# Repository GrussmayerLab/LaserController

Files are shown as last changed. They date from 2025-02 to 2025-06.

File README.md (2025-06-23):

# Laser Controller Project

## TL;DR (Quick Setup)

1. **Assemble the PCB**: 
   - Order the PCB from [JLCPCB](https://cart.jlcpcb.com) for ~$100 using the `gerber.zip`, `bom.csv`, and `laser_controller-top-pos.csv` files.
   - Use compatible [JST cables](https://www.amazon.nl/-/en/Mini-Micro-150mm-Cable-Female/dp/B01DU9OY40).

2. **Install MicroManager 2.0**:
   - Download and install [MicroManager 2.0](https://download.micro-manager.org/nightly/2.0/Windows/).

3. **Copy Files**:
   - Copy the precompiled `EMU` folder and `mmgr_dal_GrussmayerLab-LaserController.dll` into the root directory of MicroManager.

4. **Use the LaserControlGUI Plugin**:
   - Run MicroManager, open the **LaserControlGUI** plugin from **EMU**, and start controlling the laser!

---

This repository consists of the hardware, firmware, and software design for the Laser Controller system. It is divided into four main sections:

- **Electronics**: Schematic and PCB design files for the laser controller.
- **LaserControlFirmware**: C/C++ firmware for the Raspberry Pi Pico.
- **GrussmayerLab-LaserController**: C++ Micromanager Device Adapter to drive the laser controller.
- **LaserControlGUI**: Java-based plugin for Micromanager, built upon the EMU plugin.

## Table of Contents

- [Overview](#overview)
- [Folders](#folders)
  - [Electronics](#electronics)
  - [LaserControlFirmware](#lasercontrolfirmware)
  - [LaserControllerUI](#lasercontrollerui)
- [Getting Started](#getting-started)
  - [Hardware Setup](#hardware-setup)
  - [Firmware Setup](#firmware-setup)
  - [Software Setup](#software-setup)
- [Usage](#usage)
- [Contributing](#contributing)
- [License](#license)

## Overview

The Laser Controller project integrates hardware and software components to control a laser system. It consists of:

1. **Hardware**: Electronics, including a schematic and PCB design, for laser control.
2. **Firmware**: Raspberry Pi Pico firmware (C/C++) managing communication with the hardware.
3. **Software**: A Java plugin for MicroManager, based on the EMU plugin framework, along with a C++ Device Adapter for MicroManager.

## Folders

### Electronics

This folder contains the hardware designs for the laser controller:

- **Schematic**: Electrical design for the laser control system.
- **PCB Design**: Printed circuit board design files created using KiCAD.

Files in this folder:
- `schematic.kicad_sch`: Schematic file.
- `pcb.kicad_pcb`: PCB design file.

For more details, refer to the [KiCAD Documentation](https://kicad.org/documentation/).

### LaserControlFirmware

Firmware for the Raspberry Pi Pico, written in C/C++, responsible for controlling the laser system.

Files in this folder:
- `main.cpp`: Main program code.
- `CMakeLists.txt`: CMake configuration.
- `README.md`: Firmware setup instructions.

### LaserControlGUI

Java-based plugin for Micromanager, allowing control of the laser system.

Files in this folder:
- `LaserPanel.java`: Laser slide panel code.
- `MyFrame.java`: Main plugin UI containing multiple LaserPanel instances.
- `MyPlugin.java`: Main plugin class implementing the UIPlugin interface.

## Getting Started

### Hardware Setup

1. **Review Hardware Files**: Use KiCAD to view schematic and PCB design files in the `Electronics` folder.
2. **Assemble the PCB**: Using `gerber.zip`, `bom.csv`, and `laser_controller-top-pos.csv`, you can assemble your PCB at [JLCPCB](https://cart.jlcpcb.com) for approximately $100.
3. **Connect Components**: The board has **JST S3B-PH-K-S (LF)(SN)** connectors. Buy [compatible cables](https://www.amazon.nl/-/en/Mini-Micro-150mm-Cable-Female/dp/B01DU9OY40) and modify them as needed.

### Firmware Setup

1. **Flashing Precompiled Firmware**:
   - The compiled UF2 firmware is already included in the repository.
   - Hold the **BOOTSEL** button on the Raspberry Pi Pico, connect it to a PC via USB, and it will appear as a **USB drive**.
   - Copy the UF2 file to the drive, and the Pico is programmed.

2. **Optional: Building from Source**:
   If you wish to modify the firmware, install the following tools:
   - [Raspberry Pi Pico SDK](https://github.com/raspberrypi/pico-sdk)
   - [CMake](https://cmake.org/)
   - [ARM GCC Toolchain](https://developer.arm.com/tools-and-software/openSourceTools/gnu-toolchain/gnu-toolchain-r)

   Clone the repository and build:
   ```bash
   git clone https://github.com/GrussmayerLab/LaserController.git
   cd LaserControlFirmware
   mkdir build
   cd build
   cmake ..
   make
   ```

### Software Setup

1. **Install MicroManager 2.0**:
   - Download and install the latest version of [MicroManager 2.0](https://download.micro-manager.org/nightly/2.0/Windows/). Copy the precompiled `EMU` folder (provided) into the root directory of MicroManager.

2. **Install the EMU Plugin** (for source code editing):
   - If you wish to modify or extend the plugin, follow the instructions on how to install [EMU](https://jdeschamps.github.io/EMU-guide/):

3. **Install LaserControlGUI Plugin**:
   - To enable the LaserControlUI plugin, export the Java project from Eclipse into the EMU folder in MicroManager.

4. **Install the Device Adapter**:
   - Copy the `mmgr_dal_GrussmayerLab-LaserController.dll` file in the root directory of MicroManager.
   - If you need to configure or extend the device adapter, follow the [MicroManager Visual Studio setup guide](https://micro-manager.org/Visual_Studio_project_settings_for_device_adapters). After setting up your project, place `.h` files in the header folder and `.cpp` files in the source folder. Compile the project, and place the resulting `.dll` file in the root directory of MicroManager.

## Usage

1. Start MicroManager.
2. Open the **LaserControlGUI** plugin.
3. The plugin will interface with the Raspberry Pi Pico, allowing laser control via MicroManager.

## License

This project is licensed under the MIT License - see the LICENSE file for details.

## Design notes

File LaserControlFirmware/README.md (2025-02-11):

# Laser Controller Software

## Overview

Laser controller which can be controlled over serial USB via uManager custom EMU plugin.

## Installation
1. Clone the repository: `https://github.com/GrussmayerLab/LaserController.git`

2. Set up the Pico SDK:
   - Download and extract the Pico SDK from [https://github.com/raspberrypi/pico-sdk](https://github.com/raspberrypi/pico-sdk).
   - Configure the CMakeLists.txt file according to your project's requirements.
   - Install Visual Studio Code and the necessary extensions (C/C++ and CMake Tools).
   - Open the Pico SDK folder in Visual Studio Code.
   - Build the project using the provided build tasks.

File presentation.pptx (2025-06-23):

## Laser Controller

## Current Solution

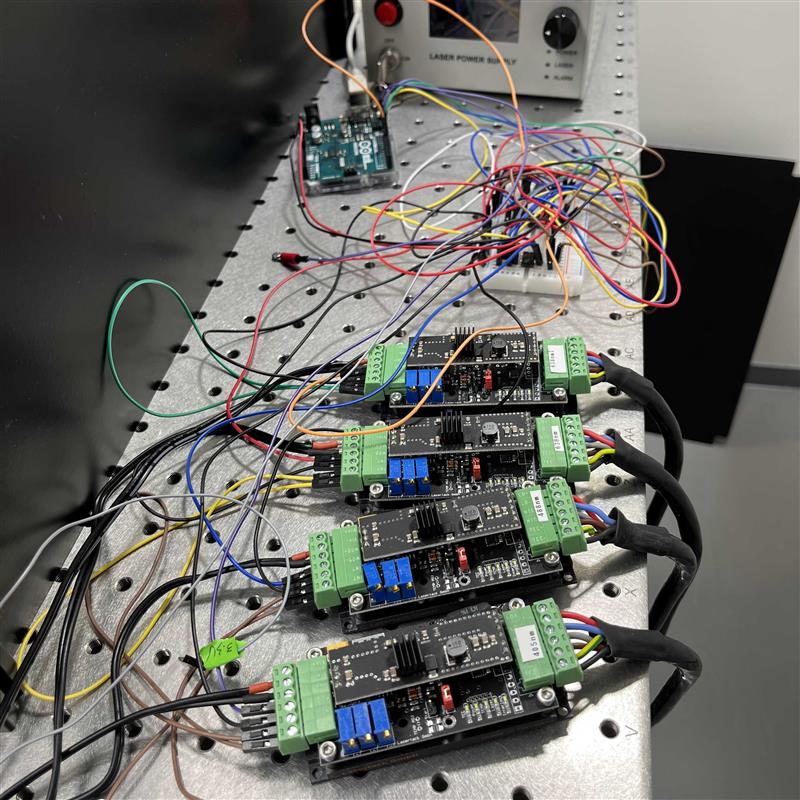
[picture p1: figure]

## Requirements

- Should be controllable in Micro-Manager
- Should be easy to install (software)
- Should be easy to build (hardware)
- Should be inexpensive (under $100)

## Hardware Design

Raspberry Pi Pico: firmware can easily be installed without requiring special tools.
The Board can be ordered at JLC PCB at a cost of ~$35 per board.

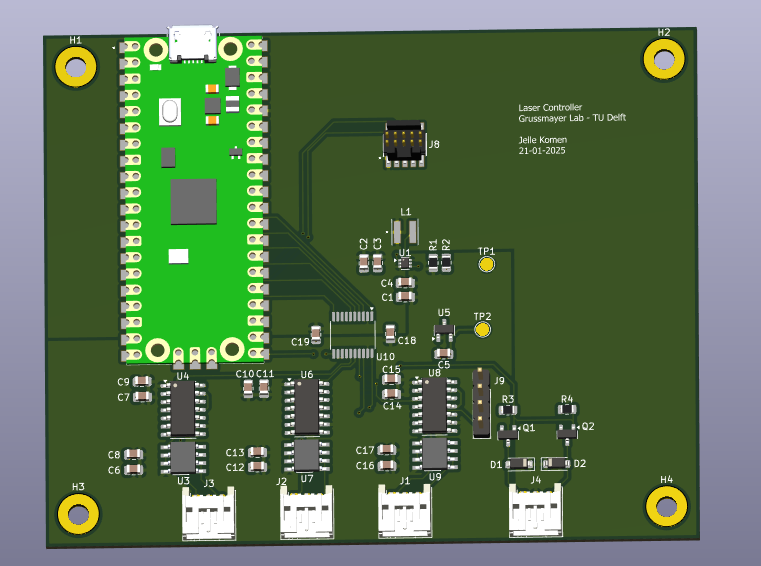
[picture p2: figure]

## Software Design

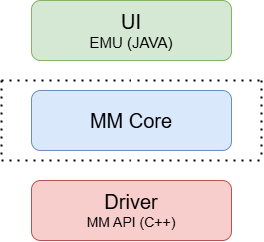
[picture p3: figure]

## Driver Installation

- Open Device Manager

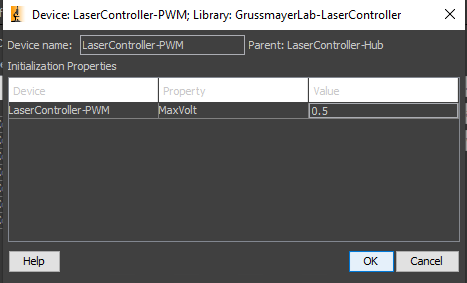
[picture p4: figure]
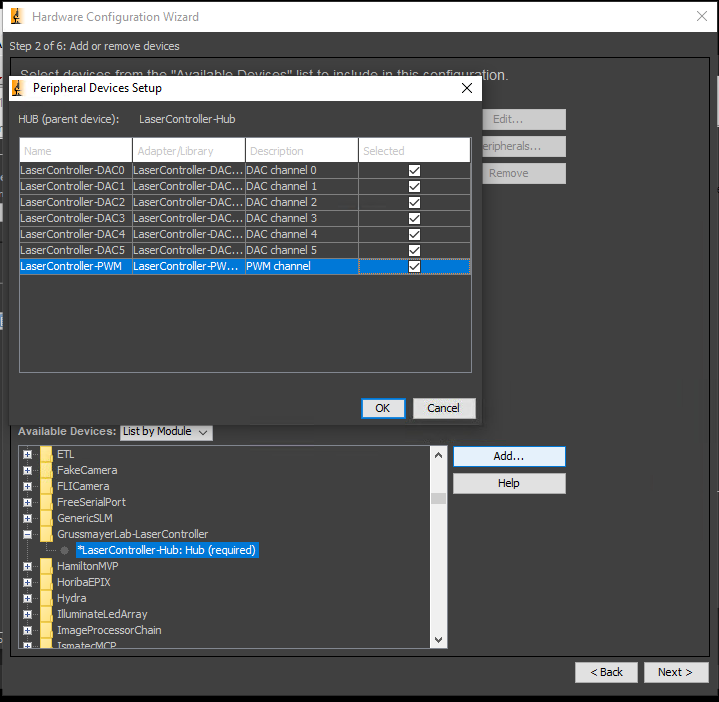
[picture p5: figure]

## User Interface

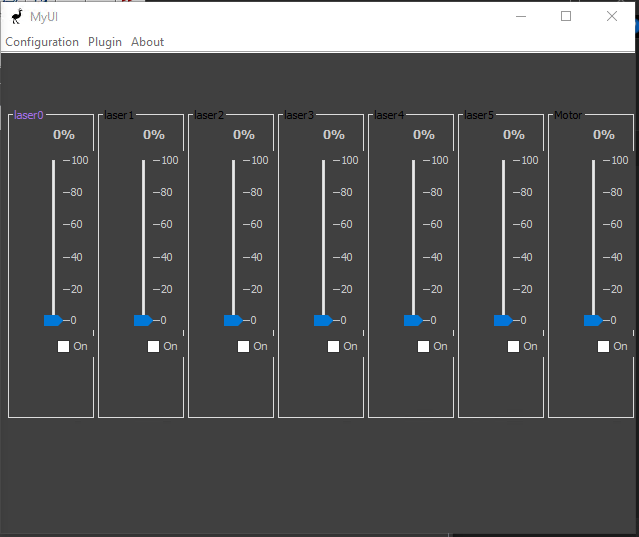
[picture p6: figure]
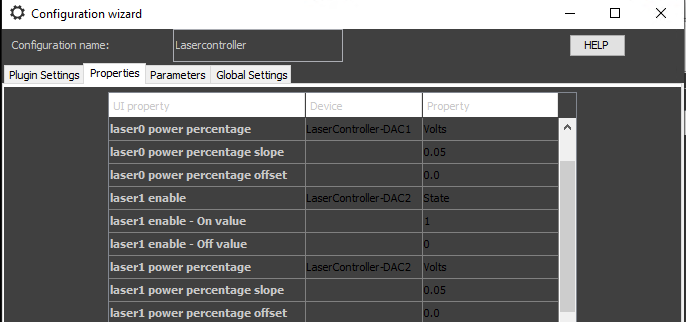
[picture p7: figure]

## Questions?

https://github.com/GrussmayerLab/LaserController

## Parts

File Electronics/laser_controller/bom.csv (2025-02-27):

Comment | Designator | Footprint | LCSC
TXS0108EPW | "U10" | "Package_SO:Texas_PW0020A_TSSOP-20_4.4x6.5mm_P0.65mm" | "C17206"
REF3025-AIDBZR | U5 | Package_TO_SOT_SMD:SOT-23-3 | C11334
MCP4922-ESL | U4,U6,U8 | Package_SO:SOIC-14_3.9x8.7mm_P1.27mm | C39851
MCP6022 | U3,U7,U9 | Package_SO:SOIC-8_5.275x5.275mm_P1.27mm | C57639
TPS61023 | U1 | Package_TO_SOT_SMD:SOT-563 | C919459
10k | R3,R4 | Resistor_SMD:R_0805_2012Metric | C149504
100k | R2 | Resistor_SMD:R_0805_2012Metric | C441992
820k | R1 | Resistor_SMD:R_0805_2012Metric | C413229
AO3400A | Q1,Q2 | Package_TO_SOT_SMD:SOT-23 | C20917
XEL4030-102MEC | L1 | parts:IND_XEL4030-102MEC | C5441341
FTSH-105-01-F-DV-P-TR | J8 | parts:SAMTEC_FTSH-105-01-F-DV-P-TR | C5136979
SM4007PL | D1,D2 | Diode_SMD:D_SOD-123 | C64898
100n | C2,C6,C7,C11,C13,C15,C17,C18,C19 | Capacitor_SMD:C_0805_2012Metric | C1711
10u | C1,C3,C4,C5,C8,C9,C10,C12,C14,C16 | Capacitor_SMD:C_0805_2012Metric | C1713
S3B-PH-K-S_LF__SN_ | "J1 | J2 | J3 | J4" | Connector_JST:JST_PH_S3B-PH-K_1x03_P2.00mm_Horizontal | C157929

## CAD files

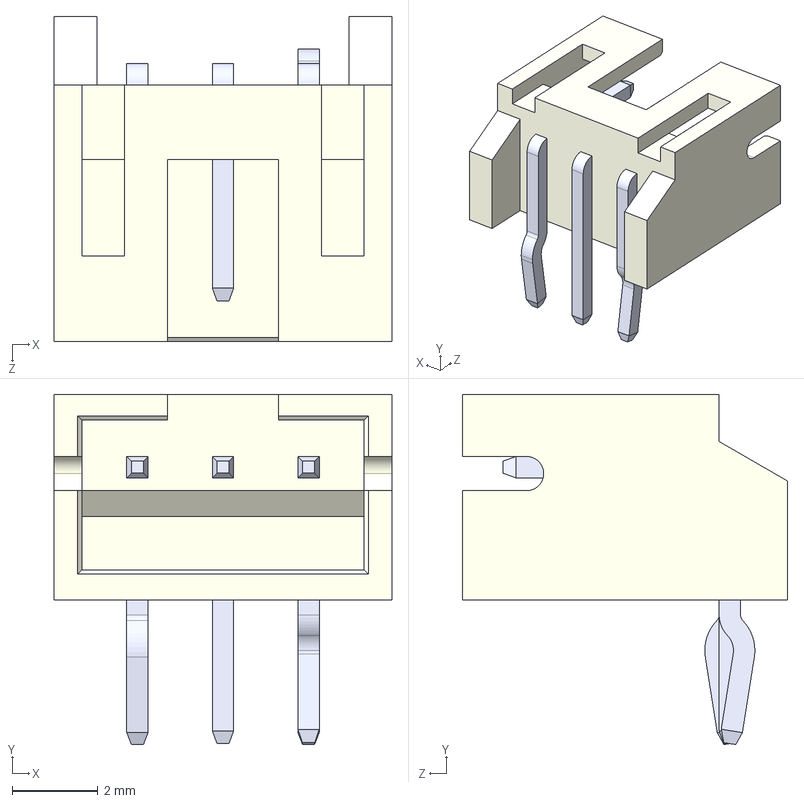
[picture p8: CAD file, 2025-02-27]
Electronics/laser_controller/parts/S3B-PH-K-S_LF__SN_.step
7.90 x 8.18 x 7.60 mm

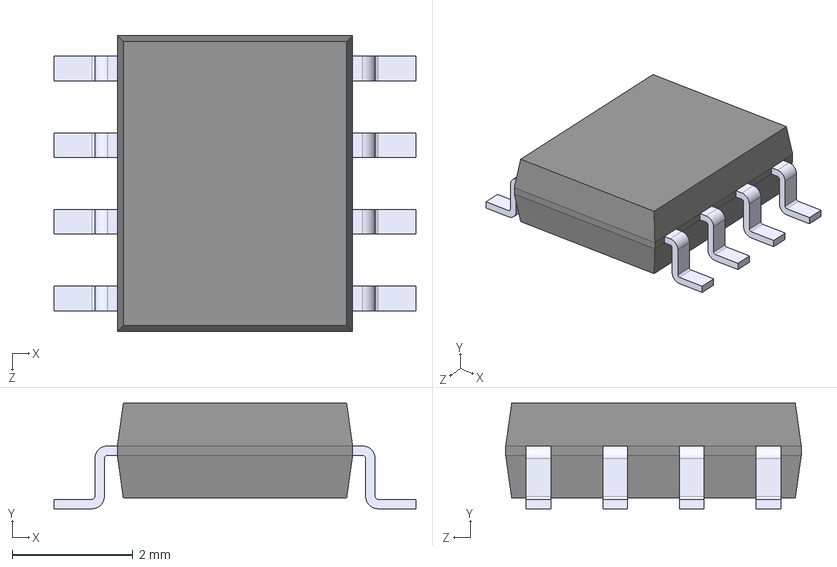
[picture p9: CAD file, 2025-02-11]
Electronics/laser_controller/parts/MCP6022T-I_SN.step
6.00 x 1.75 x 4.90 mm

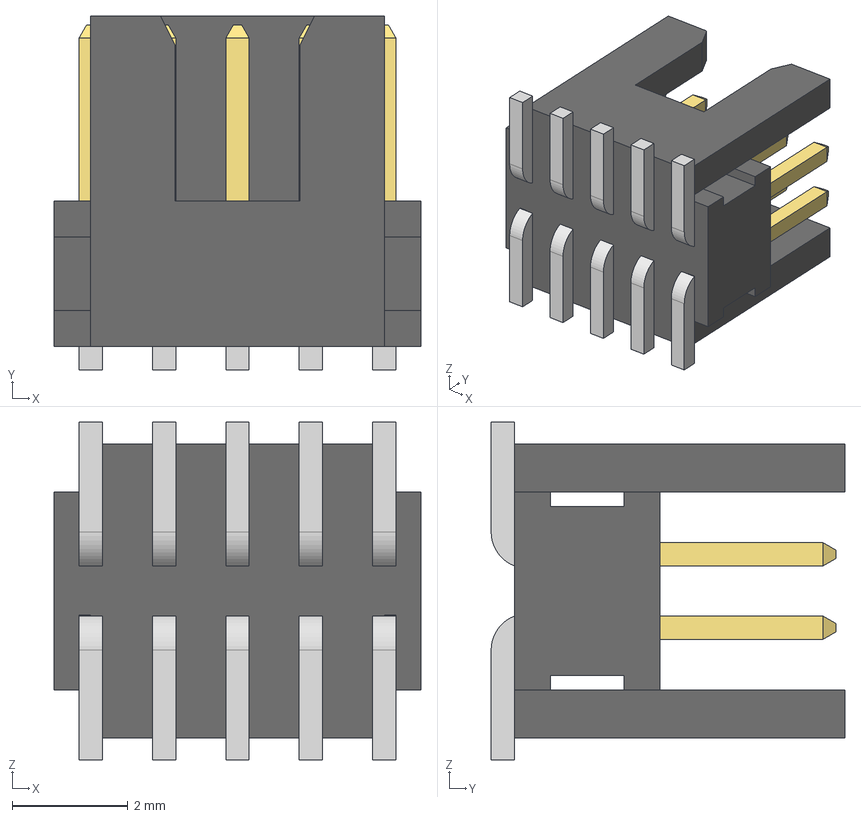
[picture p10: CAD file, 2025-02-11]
Electronics/laser_controller/parts/FTSH-105-01-F-DV-P-TR.step
6.35 x 6.12 x 5.84 mm
FTSH-105-01-F-DV-K_body
FTSH-105-01-F-DV-K_pins1
FTSH-105-01-F-DV-K_pins2

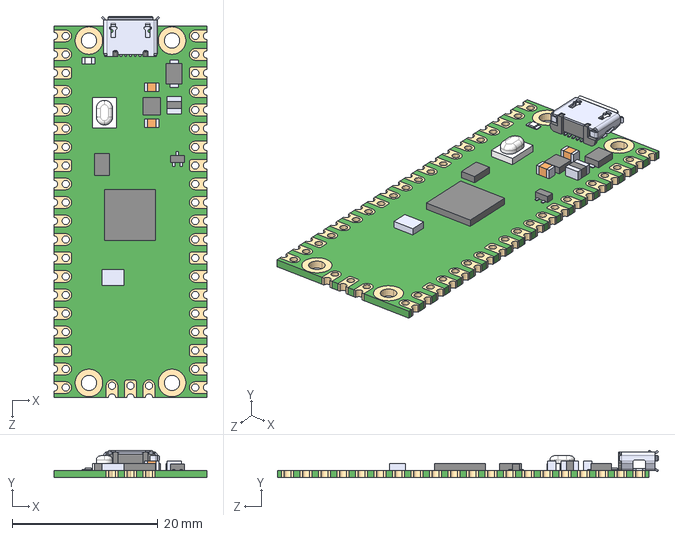
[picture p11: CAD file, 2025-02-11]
Electronics/laser_controller/parts/SC0915.step
21.0 x 3.73 x 52.3 mm

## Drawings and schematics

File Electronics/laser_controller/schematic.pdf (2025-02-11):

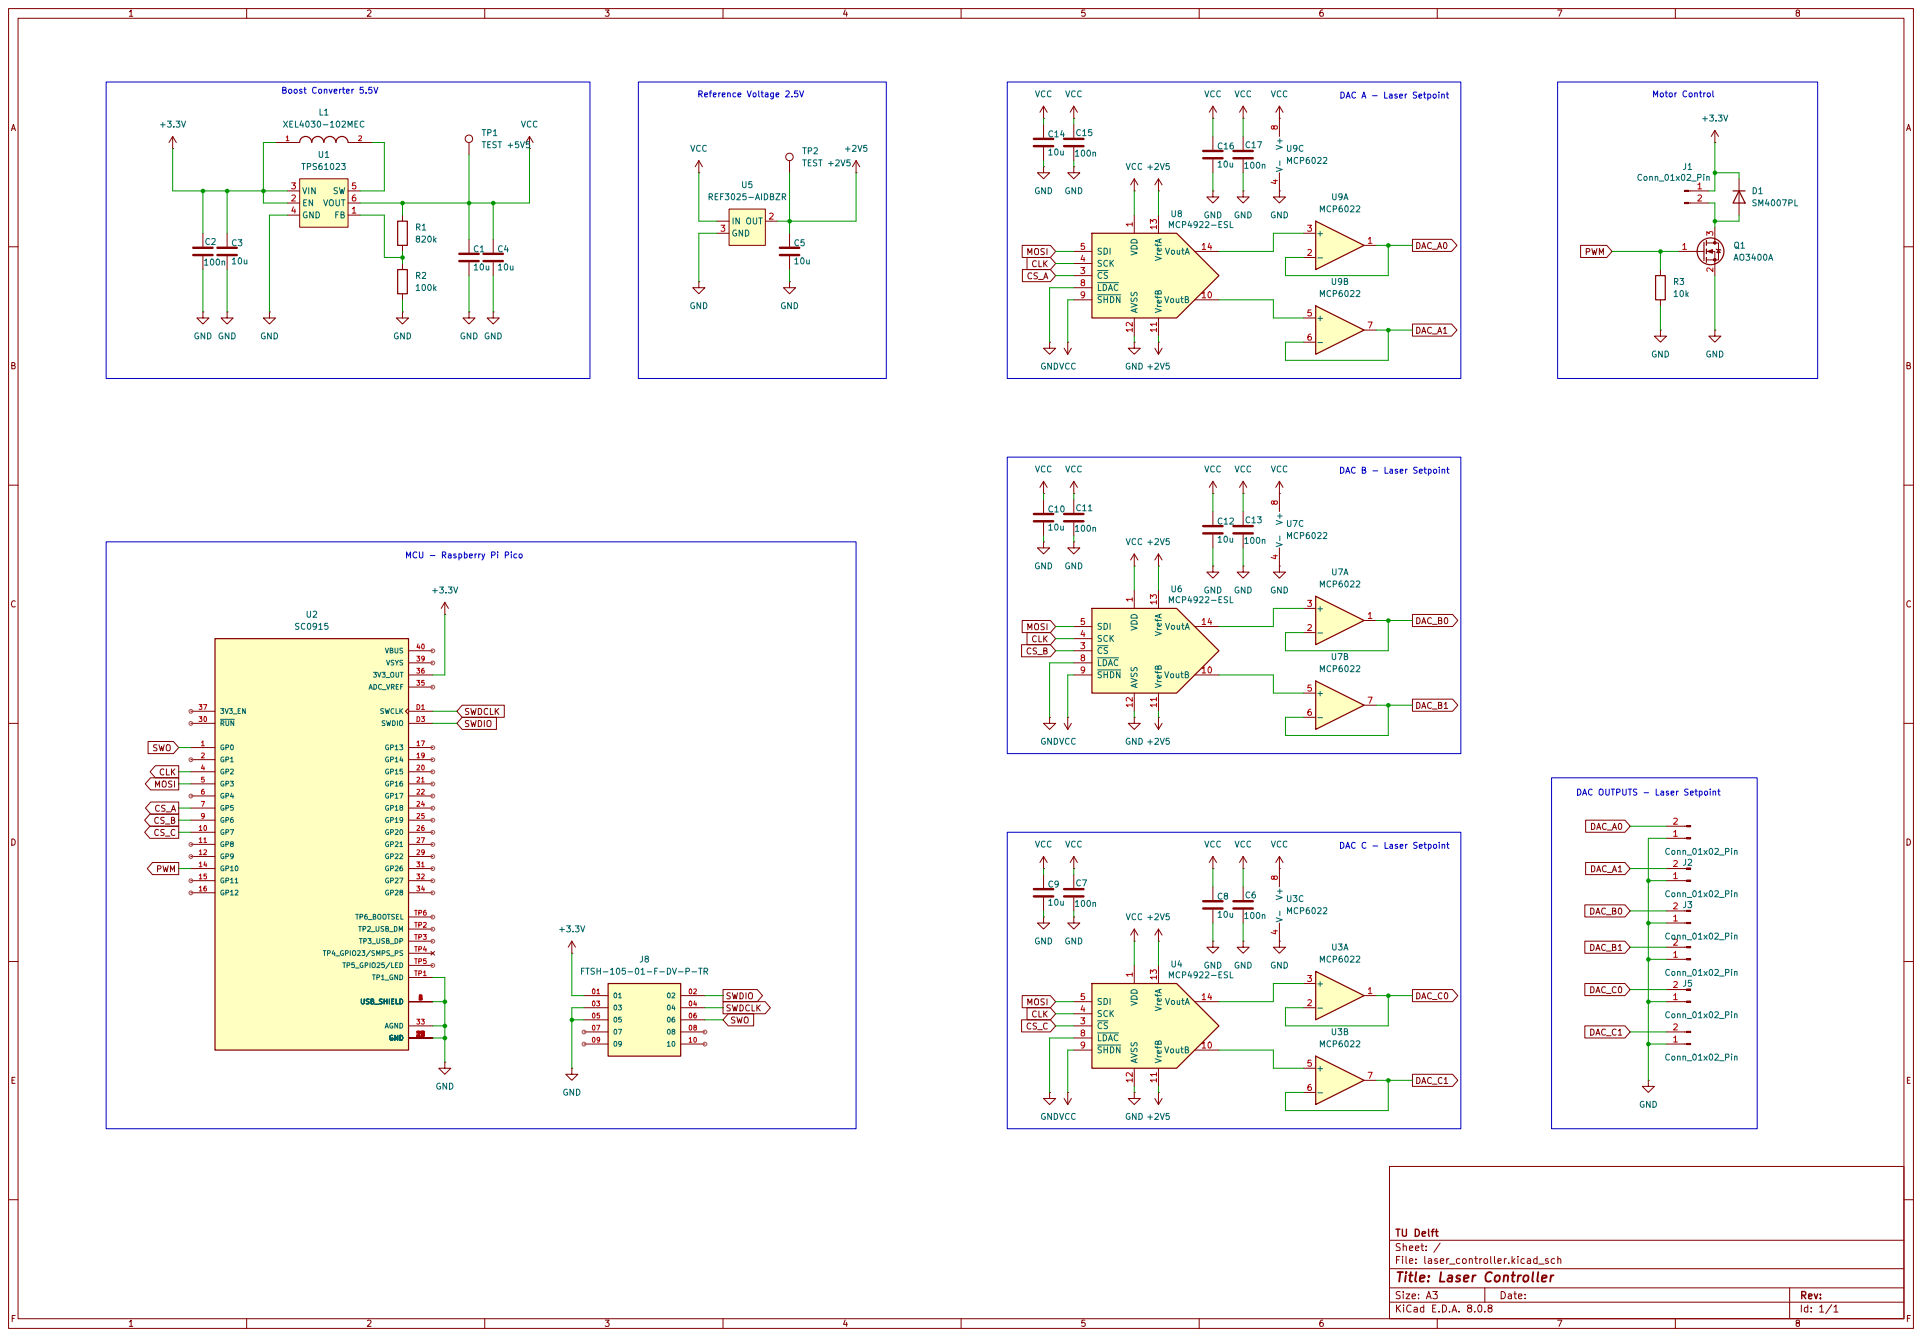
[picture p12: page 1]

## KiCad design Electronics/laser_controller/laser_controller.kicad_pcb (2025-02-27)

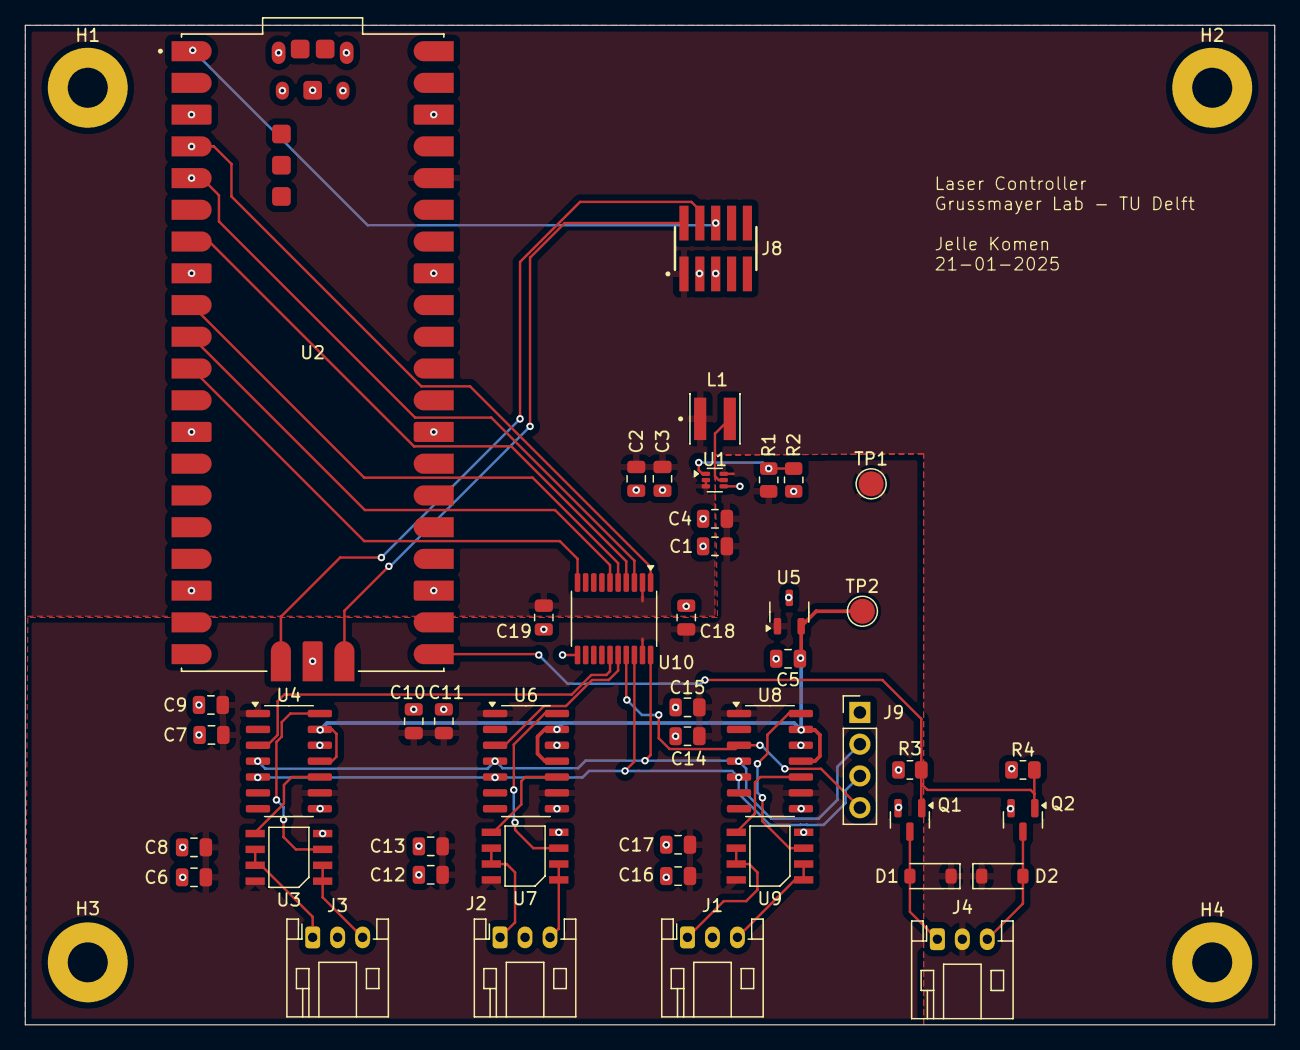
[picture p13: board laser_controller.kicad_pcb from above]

Board: 2 copper layers, 100.0 x 80.0 mm, 50 parts (0 on the bottom side), 35 nets.

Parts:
C1, C3, C4, C5, C8, C9, C10, C12, C14, C16: 10u; C_0805_2012Metric
C2, C6, C7, C11, C13, C15, C17, C18, C19: 100n; C_0805_2012Metric
D1, D2: SM4007PL; D_SOD-123
H1, H2, H3, H4: MountingHole_Pad; MountingHole_3.2mm_M3_Pad
J1, J2, J3, J4: S3B-PH-K-S_LF__SN_; JST_PH_S3B-PH-K_1x03_P2.00mm_Horizontal
J8: FTSH-105-01-F-DV-P-TR; SAMTEC_FTSH-105-01-F-DV-P-TR
J9: Conn_01x04_Pin; PinHeader_1x04_P2.54mm_Vertical
L1: XEL4030-102MEC; IND_XEL4030-102MEC
Q1, Q2: AO3400A; SOT-23
R1: 820k; R_0805_2012Metric
R2: 100k; R_0805_2012Metric
R3, R4: 10k; R_0805_2012Metric
TP1: TEST +5V5; TestPoint_Pad_D2.0mm
TP2: TEST +2V5; TestPoint_Pad_D2.0mm
U1: TPS61023; SOT-563
U2: SC0915; MODULE_SC0915
U3, U7, U9: MCP6022; SOIC-8-SN
U4, U6, U8: MCP4922-ESL; SOIC-14_3.9x8.7mm_P1.27mm
U5: REF3025-AIDBZR; SOT-23-3
U10: TXS0108EPW; Texas_PW0020A_TSSOP-20_4.4x6.5mm_P0.65mm

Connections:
+2V5: C5.1, TP2.1, U4.11 (VrefB), U4.13 (VrefA), U5.2 (OUT), U6.11 (VrefB), U6.13 (VrefA), U8.11 (VrefB), U8.13 (VrefA)
+3.3V: C2.1, C3.1, C19.1, D1.1 (K), D2.1 (K), J4.2, J8.01, L1.1, U1.2 (EN), U1.3 (VIN), U2.36 (3V3_OUT), U10.2 (VCCA)
CLK: U2.4 (GP2), U10.1 (A1)
CLK_B: J9.2, U4.4 (SCK), U6.4 (SCK), U8.4 (SCK), U10.20 (B1)
CS_A: U2.7 (GP5), U10.4 (A3)
CS_A_B: J9.4, U8.3 (~CS), U10.17 (B3)
CS_B: U2.9 (GP6), U10.5 (A4)
CS_B_B: U6.3 (~CS), U10.16 (B4)
CS_C: U2.10 (GP7), U10.6 (A5)
CS_C_B: U4.3 (~CS), U10.15 (B5)
DAC_A0: J1.3, U9.1, U9.2 (-)
DAC_A1: J1.1, U9.6 (-), U9.7
DAC_B0: J2.3, U7.1, U7.2 (-)
DAC_B1: J2.1, U7.6 (-), U7.7
DAC_C0: J3.3, U3.1, U3.2 (-)
DAC_C1: J3.1, U3.6 (-), U3.7
GND: C1.2, C2.2, C3.2, C4.2, C5.2, C6.2, C7.2, C8.2, C9.2, C10.2, C11.2, C12.2, C13.2, C14.2, C15.2, C16.2, C17.2, C18.2, C19.2, H1.1, H2.1, H3.1, H4.1, J1.2, J2.2, J3.2, J8.03, J8.05, J9.1, Q1.2 (S), Q2.2 (S), R2.2, R3.2, R4.2, U1.4 (GND), U2.3 (GND), U2.8 (GND), U2.13 (GND), U2.18 (GND), U2.23 (GND), U2.28 (GND), U2.33 (AGND), U2.38 (GND), U2.A (USB_SHIELD), U2.B (USB_SHIELD), U2.C (USB_SHIELD), U2.D (USB_SHIELD), U2.D2 (GND), U2.TP1 (TP1_GND), U3.4 (V-), U4.8 (~LDAC), U4.12 (AVSS), U5.3 (GND), U6.8 (~LDAC), U6.12 (AVSS), U7.4 (V-), U8.8 (~LDAC), U8.12 (AVSS), U9.4 (V-), U10.11 (GND)
MOSI: U2.5 (GP3), U10.3 (A2)
MOSI_B: J9.3, U4.5 (SDI), U6.5 (SDI), U8.5 (SDI), U10.18 (B2)
Motor- A: D1.2 (A), J4.1, Q1.3 (D)
Motor- B: D2.2 (A), J4.3, Q2.3 (D)
unnamed: R1.2, R2.1, U1.1 (FB)
unnamed: L1.2, U1.5 (SW)
unnamed: U3.3 (+), U4.14 (VoutA)
unnamed: U3.5 (+), U4.10 (VoutB)
unnamed: U6.14 (VoutA), U7.3 (+)
unnamed: U6.10 (VoutB), U7.5 (+)
unnamed: U8.14 (VoutA), U9.3 (+)
unnamed: U8.10 (VoutB), U9.5 (+)
OE: U2.11 (GP8), U10.10 (OE)
PWM: Q1.1 (G), Q2.1 (G), R3.1, R4.1, U2.21 (GP16)
SWDCLK: J8.04, U2.D1 (SWCLK)
SWDIO: J8.02, U2.D3 (SWDIO)
SWO: J8.06, U2.1 (GP0)
VCC: C1.1, C4.1, C6.1, C7.1, C8.1, C9.1, C10.1, C11.1, C12.1, C13.1, C14.1, C15.1, C16.1, C17.1, C18.1, R1.1, TP1.1, U1.6 (VOUT), U3.8 (V+), U4.1 (VDD), U4.9 (~SHDN), U5.1 (IN), U6.1 (VDD), U6.9 (~SHDN), U7.8 (V+), U8.1 (VDD), U8.9 (~SHDN), U9.8 (V+), U10.19 (VCCB)

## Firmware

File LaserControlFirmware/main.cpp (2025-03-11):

#include "mcp4922.h"
#include <hardware/spi.h>
#include <hardware/pwm.h>
#include <stdio.h>
#include "pico/stdlib.h"
#include <string.h> // For memset

#define CLk_FREQ 100000
#define SCLK 2
#define MOSI 3
#define CS_C 5
#define CS_B 6
#define CS_A 7
#define OE 8
#define PWM 16
#define CMD_GET_DEVICE 0x01
#define CMD_SET_LASER 0x02
#define CMD_SET_MOTOR 0x03

#define START_FLAG 0x7E
#define END_FLAG 0x7F
#define DEVICE_ID 0x01
#define RESPONSE_ERROR 0xFF
#define BUFFER_SIZE 64
#define QUEUE_SIZE 10 // Number of messages in FIFO

// FIFO Queue for messages
typedef struct
{
    uint8_t data[BUFFER_SIZE];
    int length;
} Message;

Message fifo_queue[QUEUE_SIZE];
int fifo_head = 0;
int fifo_tail = 0;

uint8_t serial_buffer[BUFFER_SIZE];
int buffer_index = 0;

void checkAndExtractMessages();
void processSerialCommand();
uint8_t calculateCRC(uint8_t *args, int argCount);
void handleGetDevice();
void handleSetLaser(uint8_t channel_id, uint16_t value);
void handleSetMotor(uint16_t value);

MCP4922 dac1(spi0, CLk_FREQ, SCLK, MOSI, CS_A);
MCP4922 dac2(spi0, CLk_FREQ, SCLK, MOSI, CS_B);
MCP4922 dac3(spi0, CLk_FREQ, SCLK, MOSI, CS_C);

// FIFO Helper Functions
bool isFIFOFull() { return ((fifo_head + 1) % QUEUE_SIZE) == fifo_tail; }
bool isFIFOEmpty() { return fifo_head == fifo_tail; }

void enqueueMessage(uint8_t *data, int length)
{
    if (!isFIFOFull())
    {
        memcpy(fifo_queue[fifo_head].data, data, length);
        fifo_queue[fifo_head].length = length;
        fifo_head = (fifo_head + 1) % QUEUE_SIZE;
    }
}

bool dequeueMessage(Message *msg)
{
    if (!isFIFOEmpty())
    {
        *msg = fifo_queue[fifo_tail];
        fifo_tail = (fifo_tail + 1) % QUEUE_SIZE;
        return true;
    }
    return false;
}

int main(void)
{
    stdio_init_all();

    // Set stdin to non-blocking mode
    setvbuf(stdin, NULL, _IONBF, 0);

    printf("Pico USB Serial Ready\n");

    gpio_init(OE);
    gpio_set_dir(OE, GPIO_OUT);
    gpio_pull_up(OE);
    gpio_put(OE, 1);

    // uint16_t test = 0xFFF;

    // dac1.analogWrite(MCP4922::channel_B, test);
    // dac2.analogWrite(MCP4922::channel_B, test);
    // dac3.analogWrite(MCP4922::channel_B, test);

    while (true)
    {
        int ch = getchar_timeout_us(1); // Poll every 1us
        if (ch != -1)
        {
            serial_buffer[buffer_index++] = (uint8_t)ch;

            if (buffer_index >= BUFFER_SIZE)
            {
                buffer_index = 0; // Prevent overflow
            }

            // Extract messages from buffer and store them in FIFO
            checkAndExtractMessages();
        }

        // Process the next available command in FIFO
        if (!isFIFOEmpty())
        {
            processSerialCommand();
        }
    }
}

void checkAndExtractMessages()
{
    int startIdx = -1;
    int endIdx = -1;

    // Scan the buffer to find the first START_FLAG and END_FLAG
    for (int i = 0; i < buffer_index; i++)
    {
        if (serial_buffer[i] == START_FLAG && startIdx == -1)
        {
            startIdx = i; // Mark the start of a valid message
        }
        if (serial_buffer[i] == END_FLAG && startIdx != -1)
        {
            endIdx = i; // Found a complete message
            int messageLength = endIdx - startIdx + 1;

            // Store the valid message in FIFO
            enqueueMessage(&serial_buffer[startIdx], messageLength);

            // Remove processed message from buffer
            memmove(serial_buffer, &serial_buffer[endIdx + 1], BUFFER_SIZE - (endIdx + 1));
            buffer_index -= (endIdx + 1);

            // Reset start/end markers and continue scanning
            startIdx = -1;
            endIdx = -1;
            i = -1; // Restart loop from beginning
        }
    }

    // If buffer is full but no complete message, reset to prevent overflow
    if (buffer_index >= BUFFER_SIZE)
    {
        buffer_index = 0;
        memset(serial_buffer, 0, sizeof(serial_buffer));
    }
}

void processSerialCommand()
{
    Message msg;
    if (!dequeueMessage(&msg))
        return;

    uint8_t command, length, receivedCRC, calculatedCRC;
    uint8_t channel_id, upper, lower;
    uint16_t value;

    if (msg.length < 4)
        return; // Ignore incomplete packets

    command = msg.data[1];
    length = msg.data[2];
    receivedCRC = msg.data[length];

    // Validate CRC
    calculatedCRC = calculateCRC(&msg.data[1], length - 1);
    if (calculatedCRC != receivedCRC)
    {
        putchar(RESPONSE_ERROR);
        return;
    }

    switch (command)
    {
    case CMD_GET_DEVICE:
        handleGetDevice();
        break;
    case CMD_SET_LASER:
        channel_id = msg.data[3];
        upper = msg.data[4];
        lower = msg.data[5];
        value = (upper << 8) + lower;
        handleSetLaser(channel_id, value);
        break;
    case CMD_SET_MOTOR:
        upper = msg.data[3];
        lower = msg.data[4];
        value = (uint16_t)(upper << 8) + lower;
        handleSetMotor(value);
        break;
    default:
        putchar(RESPONSE_ERROR);
        break;
    }
}

uint8_t calculateCRC(uint8_t *args, int argCount)
{
    uint8_t crc = 0;
    for (int i = 0; i < argCount; i++)
    {
        crc ^= args[i];
    }
    return crc;
}

void handleGetDevice()
{
    uint8_t response[] = {CMD_GET_DEVICE, 0x01, DEVICE_ID};
    uint8_t crc = calculateCRC(response, 3);

    putchar(0x7E);
    for (int i = 0; i < 3; i++)
    {
        putchar(response[i]);
    }
    putchar(crc);
    putchar(0x7F);
}

void handleSetLaser(uint8_t channel_id, uint16_t value)
{
    // Array of DAC objects
    MCP4922 *dacs[] = {&dac1, &dac1, &dac2, &dac2, &dac3, &dac3};

    // Array of corresponding channels
    MCP4922::Channel channels[] = {
        MCP4922::channel_B, MCP4922::channel_A,
        MCP4922::channel_B, MCP4922::channel_A,
        MCP4922::channel_B, MCP4922::channel_A};

    if (channel_id < 6)
    {
        dacs[channel_id]->analogWrite(channels[channel_id], value);
    }
}

void setupPWM(uint gpio, uint16_t duty_cycle)
{
    // Get the slice number for this GPIO pin
    uint slice_num = pwm_gpio_to_slice_num(gpio);
    uint channel = pwm_gpio_to_channel(gpio);

    // Set GPIO function to PWM
    gpio_set_function(gpio, GPIO_FUNC_PWM);

    // Set the PWM frequency (125 MHz / wrap)
    pwm_set_wrap(slice_num, 65535); // 16-bit resolution (0-65535)

    // Set duty cycle
    pwm_set_chan_level(slice_num, channel, duty_cycle);

    // Enable PWM
    pwm_set_enabled(slice_num, true);
}

void handleSetMotor(uint16_t value)
{
    setupPWM(PWM, value);
}

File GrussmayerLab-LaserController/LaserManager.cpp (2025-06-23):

#include "LaserManager.h"
#include "Protocol.h"
#include "DeviceBase.h" // Ensure this header is included for MM::Device
#include <sstream>
#include <cstdio>

#ifdef WIN32
#define WIN32_LEAN_AND_MEAN
#include <windows.h>
#endif

const char *g_DeviceNameHub = "LaserController-Hub";
const char *g_DeviceNameDAC = "LaserController-DAC";
const char *g_DeviceNamePWM = "LaserController-PWM";

// Global info about the state of the Arduino.  This should be folded into a class
const int g_Min_MMVersion = 1;
const int g_Max_MMVersion = 3;
const char *g_versionProp = "Version";
const char *g_normalLogicString = "Normal";
const char *g_invertedLogicString = "Inverted";

const char *g_On = "On";
const char *g_Off = "Off";

///////////////////////////////////////////////////////////////////////////////
// Exported MMDevice API
///////////////////////////////////////////////////////////////////////////////
MODULE_API void InitializeModuleData()
{
    RegisterDevice(g_DeviceNameHub, MM::HubDevice, "Hub (required)");
    RegisterDevice("LaserController-DAC0", MM::SignalIODevice, "DAC channel 0");
    RegisterDevice("LaserController-DAC1", MM::SignalIODevice, "DAC channel 1");
    RegisterDevice("LaserController-DAC2", MM::SignalIODevice, "DAC channel 2");
    RegisterDevice("LaserController-DAC3", MM::SignalIODevice, "DAC channel 3");
    RegisterDevice("LaserController-DAC4", MM::SignalIODevice, "DAC channel 4");
    //RegisterDevice("LaserController-DAC5", MM::SignalIODevice, "DAC channel 5");
    RegisterDevice(g_DeviceNamePWM, MM::SignalIODevice, "PWM channel");
}

MODULE_API MM::Device *CreateDevice(const char *deviceName)
{
    if (deviceName == 0)
        return 0;

    if (strcmp(deviceName, g_DeviceNameHub) == 0)
    {
        return new LaserManagerHub;
    }
    else if (strcmp(deviceName, "LaserController-DAC0") == 0)
    {
        return new LaserManagerDAC(1);
    }
    else if (strcmp(deviceName, "LaserController-DAC1") == 0)
    {
        return new LaserManagerDAC(2);
    }
    else if (strcmp(deviceName, "LaserController-DAC2") == 0)
    {
        return new LaserManagerDAC(3);
    }
    else if (strcmp(deviceName, "LaserController-DAC3") == 0)
    {
        return new LaserManagerDAC(4);
    }
    else if (strcmp(deviceName, "LaserController-DAC4") == 0)
    {
        return new LaserManagerDAC(5);
    }
    else if (strcmp(deviceName, "LaserController-DAC5") == 0)
    {
        return new LaserManagerDAC(6);
    }
    else if (strcmp(deviceName, g_DeviceNamePWM) == 0)
    {
        return new LaserManagerPWM(1);
    }
    return 0;
}

MODULE_API void DeleteDevice(MM::Device *pDevice)
{
    delete pDevice;
}

LaserManagerHub::LaserManagerHub() : initialized_(false),
                                     version_(0)
{
    portAvailable_ = false;
    invertedLogic_ = false;
    timedOutputActive_ = false;
    std::cout << "test1" << std::endl;

    InitializeDefaultErrorMessages();

    SetErrorText(ERR_PORT_OPEN_FAILED, "Failed opening USB device");
    SetErrorText(ERR_BOARD_NOT_FOUND, "Did not find an board with the correct firmware.  Is the Arduino board connected to this serial port?");
    SetErrorText(ERR_NO_PORT_SET, "Hub Device not found.  The Hub device is needed to create this device");
    std::ostringstream errorText;
    errorText << "The firmware version on the board is not compatible with this adapter.  Please use firmware version ";
    errorText << g_Min_MMVersion << " to " << g_Max_MMVersion;
    SetErrorText(ERR_VERSION_MISMATCH, errorText.str().c_str());
    std::cout << "test2" << std::endl;

    CPropertyAction *pAct = new CPropertyAction(this, &LaserManagerHub::OnPort);
    CreateProperty(MM::g_Keyword_Port, "Undefined", MM::String, false, pAct, true);
    std::cout << "test3" << std::endl;
}

LaserManagerHub::~LaserManagerHub()
{
    Shutdown();
}

void LaserManagerHub::GetName(char *Name) const
{
    CDeviceUtils::CopyLimitedString(Name, g_DeviceNameHub);
}

bool LaserManagerHub::Busy()
{
    return false;
}

int LaserManagerHub::GetControllerVersion(int &version)
{
    std::vector<uint8_t> message = protocol_.createGetDeviceMessage();

    int ret = WriteToComPort(port_.c_str(), message.data(), static_cast<unsigned int>(message.size()));
    if (ret != DEVICE_OK)
        return ret;

    std::string ans;

    ret = GetSerialAnswer(port_.c_str(), "\x7F", ans);
    ans = ans + "\x7F";
    std::vector<uint8_t> buffer(ans.begin(), ans.end());
    std::ostringstream oss;
    for (uint8_t b : buffer)
    {
        oss << std::hex << std::setw(2) << std::setfill('0') << static_cast<int>(b) << " ";
    }
    LogMessage("Message: " + oss.str(), true);

    bool success = protocol_.validateDeviceMessage(buffer);

    version = 1;

    if (success)
        return DEVICE_OK;
    else
        LogMessage(protocol_.getError());
    return DEVICE_NOT_CONNECTED;
}

bool LaserManagerHub::SupportsDeviceDetection(void)
{
    return true;
}

MM::DeviceDetectionStatus LaserManagerHub::DetectDevice(void)
{
    if (initialized_)
        return MM::CanCommunicate;

    // all conditions must be satisfied...
    MM::DeviceDetectionStatus result = MM::Misconfigured;
    char answerTO[MM::MaxStrLength];

    try
    {
        std::string portLowerCase = port_;
        for (std::string::iterator its = portLowerCase.begin(); its != portLowerCase.end(); ++its)
        {
            *its = (char)tolower(*its);
        }
        if (0 < portLowerCase.length() && 0 != portLowerCase.compare("undefined") && 0 != portLowerCase.compare("unknown"))
        {
            result = MM::CanNotCommunicate;
            // record the default answer time out
            GetCoreCallback()->GetDeviceProperty(port_.c_str(), "AnswerTimeout", answerTO);

            // device specific default communication parameters
            GetCoreCallback()->SetDeviceProperty(port_.c_str(), MM::g_Keyword_Handshaking, g_Off);
            GetCoreCallback()->SetDeviceProperty(port_.c_str(), MM::g_Keyword_BaudRate, "115200");
            GetCoreCallback()->SetDeviceProperty(port_.c_str(), MM::g_Keyword_StopBits, "1");
            // Arduino timed out in GetControllerVersion even if AnswerTimeout  = 300 ms
            GetCoreCallback()->SetDeviceProperty(port_.c_str(), "AnswerTimeout", "500.0");
            GetCoreCallback()->SetDeviceProperty(port_.c_str(), "DelayBetweenCharsMs", "0");
            MM::Device *pS = GetCoreCallback()->GetDevice(this, port_.c_str());
            pS->Initialize();
            // The first second or so after opening the serial port, the Arduino is waiting for firmwareupgrades.  Simply sleep 1 second.
            CDeviceUtils::SleepMs(1000);
            const std::lock_guard<std::mutex> lock(mutex_);
            PurgeComPort(port_.c_str());
            int v = 0;
            int ret = GetControllerVersion(v);
            // later, Initialize will explicitly check the version #
            if (DEVICE_OK != ret)
            {
                LogMessageCode(ret, true);
            }
            else
            {
                // to succeed must reach here....
                result = MM::CanCommunicate;
            }
            pS->Shutdown();
            // always restore the AnswerTimeout to the default
            GetCoreCallback()->SetDeviceProperty(port_.c_str(), "AnswerTimeout", answerTO);
        }
    }
    catch (...)
    {
        LogMessage("Exception in DetectDevice!", false);
    }

    return result;
}

int LaserManagerHub::Initialize()
{
    std::cout << "test" << std::endl;

    // Name
    int ret = CreateProperty(MM::g_Keyword_Name, g_DeviceNameHub, MM::String, true);
    if (DEVICE_OK != ret)
        return ret;

    // The first second or so after opening the serial port, the Arduino is waiting for firmwareupgrades.  Simply sleep 1 second.
    CDeviceUtils::SleepMs(1000);

    const std::lock_guard<std::mutex> lock(mutex_);

    // Check that we have a controller:
    PurgeComPort(port_.c_str());
    ret = GetControllerVersion(version_);
    if (DEVICE_OK != ret)
    {
        std::cout << "get version error" << std::endl;
        return ret;
    }

    CPropertyAction *pAct = new CPropertyAction(this, &LaserManagerHub::OnVersion);

    CreateProperty(g_versionProp, "1.0", MM::Integer, true, pAct);

    initialized_ = true;
    return DEVICE_OK;
}
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

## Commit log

2025-02-27 fixed too many bugs
    [S3B-PH-K-S-LF--SN---3DModel-STEP-56544.STEP, S3B-PH-K-S_LF__SN_.step, bom.csv, laser_controller-B_Cu.gbr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]
2025-03-11 added device controller c++ layer
2025-03-11 added device controller
2025-06-23 remove laser 6

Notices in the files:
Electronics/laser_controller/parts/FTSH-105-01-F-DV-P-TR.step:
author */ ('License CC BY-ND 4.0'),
